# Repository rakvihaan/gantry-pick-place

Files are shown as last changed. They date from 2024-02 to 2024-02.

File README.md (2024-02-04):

# Gantry Robot for Diagnostics Laboratory Automation

A gantry robot built for automated archiving of vacuum tubes.


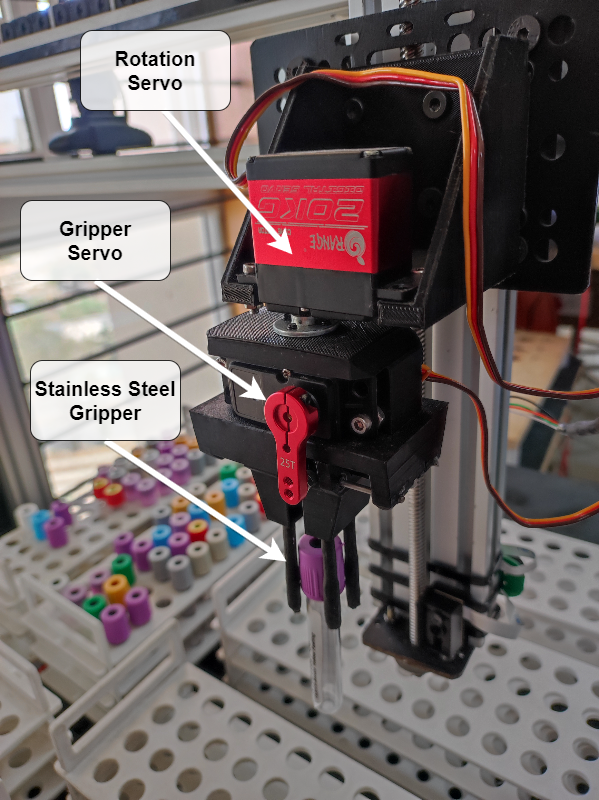
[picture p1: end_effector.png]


<br>
The hardware is built using aluminum extrusions and mild steel plates for various mounts.
Arduino Mega is used as the microcontroller with DRV8825 stepper motors drivers to drive the stepper motors.

This project also implements the application of object detection in identifying the vacuum tubes. The methodology involves training a model on annotated datasets, employing YOLO algorithm and PyTorch. Leveraging computer vision techniques, the system aims to accurately locate the vacuum tubes and the empty slots through real-time image feed.

- Has a workspace of 600 x 500 x 130 mm
- Three linear axes with a linear velocity range of
  - X-axis: 90-200 mm/s
  - Y-axis: 100-210 mm/s
  - Z-axis: 30-50 mm/s
- The three linear actuators and the wrist with the end effector with two degrees of freedom contribute to the 5-DOF design of the gantry robot
- The Z and Y axes are actuated using stepper motors and belt drive, while the X axis is actuated using a stepper motor and lead screw mechanism.
- A 3D printed end effector with stainless steel ends

## Python Scripts
- Clone the repo.
- Change pins and stepper motors speed and acceleration as per requirements in the [gantry.cpp](arduino_code/gantry.cpp) file.
- Upload the Arduino Code in the [arduino_code](arduino_code) folder.
- run the main.py file.
- Home the gantry before running any command.

## Future Improvements
- [ ] Replacing idler pulleys with optical encoders, can be used to keep track of the position.
- [ ] Replacing stepper motors with better motors with hugh torque at higher rpm.
- [ ] Realtime dynamic coordinates from image processing.
- [ ] Improve X-Axis to increase vertical workspace.

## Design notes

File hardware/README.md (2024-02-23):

# Hardware and Electrical Components BOM

| Item                               | Qty | Link |
| ---------------------------------- | :-: | :--: |
| **Hardware Components**            |     |      |
| Aluminum Extrusion                 |     |      |
| Delrin Roller Wheels               | 20  |      |
| T-nuts                             | 50  |      |
| Extrusion Brackets                 | 15  |      |
| GT2 Pulley                         |  3  |      |
| GT2 Idler Pulley                   |  3  |      |
| GT2 6mm width belt (2m)            |  2  |      |
| Lead Screw (8mm Pitch) (500mm)     |  1  |      |
| Lead Screw Block                   |  1  |      |
| Shaft Coupler                      |  1  |      |
| NEMA17 Motor mounts                |  4  |      |
| Idler Pulley mounts                |  3  |      |
| Z-Axis platform                    |  2  |      |
| 40mm Aluminium Spacers             |  3  |      |
| 90 deg Gantry bracket for Z-Axis   |  2  |      |
| Gantry bracket for Z-Axis          |  2  |      |
| 90 deg Extrusion Bracket           |  2  |      |
| Y-Axis Platform                    |  1  |      |
| X-Axis Platform                    |  1  |      |
| Servo bracket                      |  1  |      |
| Stainless Steel rods 3mm (75mm)    |  2  |      |
| Stainless Steel rods 1.2mm (100mm) |  2  |      |
| **Electrical Components**          |     |      |
| Stepper Motors (7.2 N-cm)           |  4  |      |
| DRV8825 Drivers                    |  4  |      |
| Limit Switches                     |  3  |      |
| CNC Shield                         |  1  |      |
| Arduino Mega                       |  1  |      |
| Barcode Scanner                    |  2  |      |
| Camera                             |  1  |      |
| Servos                             |  2  |      |

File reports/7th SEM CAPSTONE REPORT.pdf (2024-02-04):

(Established under Karnataka Act No. 16 of 2013) 100-ft Ring Road, Bengaluru – 560 085, Karnataka, India

### Report on Project

## “Archiving of Lab Samples using a Pick and Place Gantry robot in a Diagnostic Lab”

### Submitted by

Sumukh Marathe (PES1UG20EE068)
Vineet N Patil | (PES1UG20EE074)
N Ananya | (PES1UG20EE100)
Shreshta Srinivas (PES1UG20EE111)

### AUG - DEC 2023

Under the Guidance of
Dr. Venkatarangan MJ
Professor
Department of Electrical and Electronics PES University
Bengaluru

FACULTY OF ENGINEERING
DEPARTMENT OF ELECTRICAL AND ELECTRONICS
B. TECH IN EEE

FACULTY OF ENGINEERING

DEPARTMENT OF ELECTRICAL AND ELECTRONICS BACHELOR OF TECHNOLOGY

## CERTIFICATE

This is to certify that the Dissertation entitled

## “Archiving of Lab Samples using Pick and Place Gantry robot in a Diagnostic Lab”

Is a Bonafide work carried out by

Sumukh Marathe (PES1UG20EE068)
Vineet N Patil | (PES1UG20EE074)
N Ananya | (PES1UG20EE100)
Shreshta Srinivas (PES1UG20EE111)

In partial fulfilment for the completion of 7

th semester course work in the Program of Study
B. Tech in Electrical and Electronics Engineering (Embedded Systems) under rules and regulations of PES University, Bengaluru during the period Aug 2023 – Dec 2023. It is certified that all corrections/suggestions indicated for internal assessment have been incorporated in the report. The dissertation has been approved as it satisfies the 7th semester academic requirements in respect of project work.

### DECLARATION

We Sumukh Marathe (PES1UG20EE068), Vineet N Patil (PES1UG20EE074),N Ananya (PES1UG20EE100) and Shreshta Srinivas P R (PES1UG20EE111) hereby declare that the project entitled, “Archiving of Lab Samples using Pickand Place Gantry robot in a Diagnostic Lab”, is an original work done by us underthe guidance of Dr.Venkatarangan M J, Professor, Dept. of EEE, and is being submitted in fulfilment of the requirements for completion of 7th Semester course work in the Program of Study B.Tech in Electrical and Electronics Engineering.

PLACE: BENGALURU
DATE:

### ACKNOWLEDGMENT

We extend our deep sense of gratitude and sincere thanks to our chairman Dr.
M. R. Doreswamy (Founder, Chancellor – PES University), Prof. Jawahar Doreswamy, Pro-Chancellor of PES University and Dr. J Surya Prasad, the Vice Chancellor of PES University for giving us an opportunity to be a student of this reputed institution.

We extend our respect to our Principal Dr. K.S. Sridhar for his valuablesupport to conduct this Project under PES institution.

It is our privilege to thank the Chairperson of the Department Dr. Keshavan B.K., department of Electrical and Electronics Engineering for his support and guidance for doing our Project.

We express our sincere gratitude to our guide Dr. Venkatarangan M J for his valuable guidance and suggestion, technically and logically for doing our Project work.

We also express our gratitude to all our faculty members, parents and fellow mates who have helped us to carry out this work. Last but not the least, We thank almighty God for his blessings showered on us during this Project period.

### ABSTRACT

Archiving lab samples within a diagnostic laboratory involves the identification, labelling, and preservation of diverse bodily fluids or tissues for future reference. Adhering to precise protocols is essential in ensuring the integrity of archived samples, as human involvement may introduce inaccuracies. To address this concern, an automated robot has been developed through collaboration with and funding from Anand-Neuberg Diagnostics.

Gantry robots, also known as linear robots, are a type of industrial robot specifically designed for tasks such as picking and placing, assembly, and inspection across various industries. The objective of this project is to create and implement a gantry robot for a pick-and-place application, specifically for archiving vacuum tubes within a diagnostic laboratory. The robot operateswithin a flexible workspace, executing tasks such as picking, scanning, and placing vacuum tubes into designated crates.

The project initially utilised a Gantry Robot for transferring vacuum tubes between trays. An end effector, equipped with a precise gripper, was developed to ensure accurate pick-and-place movements. The robot's control system was optimised to delicately handle vacuum tubes, considering the spacing between tubes in the tray to prevent disruptions to adjacent samples.

Gantry robot is fabricated with the needed hardware and software interfaces. In terms of hardware, the robot needed a camera and bar-code scanner as sensors while the actuation is based on stepper motors with 5 degrees of freedom. Limit switches have been added for ensuring that it goes to a homing position on every restart of the system.

This project also implements the application of object detection in identifying the vacuum tubes. The methodology involves training a model on annotated datasets, employing YOLO algorithm and PyTorch. Leveraging computer vision techniques, the system aims to accurately locate the vacuum tubes and the empty slots through real-time image feed.

A 5 DOF gantry robot was designed and built using aluminium extrusion which helps in archiving of the vacuum tubes from 4 source racks to 5 destination racks, using Digital Image Processing. The tubes are picked, scanned and placedin their designated slots by the order of the Library Information System (LIS). The average cycle time to achieve the mentioned application is 20 seconds.

### CONTENTS

1. INTRODUCTION | 8
1.1. BACKGROUND | 8
1.2. PROBLEM STATEMENT | 8
1.3. OBJECTIVES/DELIVERABLES | 8
1.4. ARCHIVING & ITS SIGNIFICANCE | 8
2. LITERATURE SURVEY | 9

### 3. USE CASES FOR THE PROJECT AND COMPONENT

IDENTIFICATION | 12
3.1. ARCHIVING FUNCTIONALITY OF THE PROPOSED PROJECT | 12
3.2. USE CASE STEPS FOR PICK AND PLACE | 13
4. HARDWARE AND SOFTWARE ARCHITECTURE | 14
4.1. BLOCK DIAGRAMS | 14
4.2. MECHANICAL STRUCTURE AND OBJECTS | 15
4.2.1. HARDWARE USED | 16
4.2.2. SOFTWARE USED | 17
4.3. EVOLUTION OF END EFFECTOR | 17
5. ROBOT FABRICATION EXPENSES | 20
6. SW TOOLS AND HW INFRASTRUCTURE | 22
6.1. SW TOOLS | 22
6.2. MICROCONTROLLER, ACTUATORS AND SENSORS | 23
6.3. DESIGN PARAMETERS FOR AXES | 30
7. DATASET GENERATION | 31
8. OBJECT DETECTION | 33
8.1. ONE STAGE OBJECT DETECTORS | 33
8.2. WORKING OF YOLO | 35
8.2.1. RESIDUAL BLOCKS | 35
8.2.2. BOUNDING BOX REGRESSION or NON-MAXIMAL SUPPRESSION (NMS) | 35
8.2.3. INTERSECTION OF UNION | 36
8.3. YOLO MODELS | 36
8.4. YOLOV5 MODEL VERSIONS | 37
8.5. REAL TIME DETECTION OF VACUUM TUBES | 38
8.6. GENERATION OF MATRIX USING PYTHON CODE | 39
9. SOFTWARE FLOWCHART | 40
10. RESULTS | 41
10.1. GANTRY | 41
10.2. RECORDINGS | 43
10.3. CONSTRAINTS OBSERVED | 43
11. CONCLUSION | 44
12. FUTURE SCOPE | 44
13. REFERENCES | 44

TABLE OF FIGURES

Figure 1 - Moving table in X axis and couple of linear bearing on sides | 11
Figure 2 - General Block Diagram | 15
Figure 3 - Detailed Block Diagram | 15
Figure 4 - 3D view | 16
Figure 5 - Rack | 16
Figure 6 - Vacuum Tube | 16
Figure 7 – Initial End Gripper | 18
Figure 8 – Final End Gripper | 19
Figure 9 – End Gripper | 19
Table 1 - Cost Chart | 21
Figure 10 – Stepper Motor | 25
Figure 11 – Servo Motor | 25
Figure 12 – Arduino Mega | 26
Figure 13 – CNC Shield | 26
Figure 14 – DRV 8825 Driver | 27
Figure 15 – Inside a Limit Switch | 28
Figure 16 – Mechanical Limit Switch | 28
Figure 17 – AmazonBasics Camera | 29
Figure 18 – Barcode Scanner | 29
Figure 19 - Annotation by drawing bounding boxes | 32
Figure 20 - Preprocessing | 32
Figure 21 - Augmentation | 33
Figure 22 - One stage object detectors | 34
Figure 23 - Two stage object detector | 34
Figure 24 – Residual Blocks | 35
Figure 25 – Bounding Box | 36
Figure 26 - Performance Comparison | 37
Figure 27 - YOLO Model Comparison | 37
Figure 28 - Results obtained after training the YOLO v5x model for 195 epochs | 38
Figure 29 - Real time detection of tubes | 38
Figure 30 – Matrix Generated | 39
Figure 31 - Software Block diagram | 40
Figure 32 - Side view | 41
Figure 33 - End Gripper | 41
Figure 33 - Z axis | 42
Table 2 - Cycle time recordings | 43
Table 3 - Trials | 43

Archiving of Lab Samples using Pick and Place Gantry robot in a Diagnostic Lab

Dept. of Electrical & Electronics Engineering, PES University | Page 8

### 1. INTRODUCTION

### 1.1. BACKGROUND

In a diagnostic laboratory, vacuum tube samples are routinely collected from patients to perform various medical tests to diagnose diseases, monitor disease progression,and assess treatment effectiveness. These samples could include blood, urine, cerebrospinal fluid, sputum, and other bodily fluids or tissues.

The archiving of vacuum tube samples refers to the process of preserving these samples for future reference or analysis. This is important because, in some cases, it may be necessary to retest a sample or compare it with previous test results to detect changes in the patient's condition or disease progression.

### 1.2. PROBLEM STATEMENT

It is important to follow proper protocols for archiving samples to ensure their integrity. This includes labelling each sample with a unique identifier, storing them in a secure and temperature-controlled environment, and tracking their location and storage duration. Human involvement might result in inaccuracies. This system shouldaddress the challenges such as precise tube identification, safe handling, quicker operation, and seamless integration with existing laboratory workflow. To resolve this we are developing an automated gantry robot.

### 1.3. OBJECTIVES/DELIVERABLES

- Utilising Image Processing with Machine Learning techniques, a highly effective gantry robot for vacuum tubes
- Faster and extremely accurate archiving of samples
- Reduction of human workload

Dept. of Electrical & Electronics Engineering, PES University | Page 9

### 1.4. ARCHIVING & ITS SIGNIFICANCE

The significance of archiving lab samples lies in the fact that they can be used for further research or analysis in the future. For example, if new testing methods or technologies are developed, samples can be retrieved from the archive and analysed using the new methods, potentially leading to new insights or discoveries. Additionally, samples may be needed for quality control purposes, such as to verify the accuracy and consistency of test results over time.

Archiving lab samples is also important for meeting regulatory requirements and ensuring the integrity of research data. In many cases, regulatory agencies require that samples be retained for a certain period of time as part of the documentation process. Archiving samples can also help prevent data loss due to equipment failure, natural disasters, or other unforeseen events.

There are several reasons why archiving is important in a diagnostic lab:

a. Quality control: Archiving helps to ensure the accuracy and reliability of test results by providing a record of previous test results and enabling the lab to monitor and track the performance of its testing procedures and equipment over time.
b. Compliance: Many regulatory agencies require diagnostic labs to maintain accurate records of their testing processes and results, and failure to do so can result in fines, legal liability, or loss of accreditation.
c. Research and development: Archiving can provide a valuable resource for researchers and developers working on new diagnostic tests and treatments. By maintaining a comprehensive archive of patient samples and data, labs can contribute to the development of new treatments and therapies that could benefit patients in the future.
d. Patient care: Archiving allows for the ongoing monitoring of patient healthand provides a valuable resource for healthcare providers to make informed decisions about patient care based on previous test results and medical history.

Dept. of Electrical & Electronics Engineering, PES University | Page 10

### 2. LITERATURE SURVEY

Paper [1] : "Evolution of YOLO-V5 Algorithm for Object Detection: Automated Detection of Library Books and Performance validation of Dataset,"

The paper discusses the implementation and evaluation of the You Only Look Once (YOLO) version 5 algorithm for object detection, specifically for the automated detection of library books. The authors explain the steps involved in the training of the YOLOv5 algorithm using a dataset of library book images. The dataset was created by capturing images of library books using a smartphone camera and manually labelling them. The trained model was then evaluated for its performance on the detection of library books. The authors report an average precision of 0.9535 for the YOLOv5 algorithm. They conclude that the YOLOv5 algorithm is an efficient and accurate tool for automated object detection and can be used in various applications, including library book detection.

Paper[2] : “Object Detection Method for Grasping Robot Based on Improved YOLOv5”

The paper proposes a new object detection method for a grasping robot based on the improved YOLOv5 (You Only Look Once version 5) algorithm. The authors argue that the traditional YOLOv5 algorithm has limitations in detecting small objects and lacks robustness in complex scenarios. To address these limitations, the authors propose an improved YOLOv5 algorithm that incorporates a new loss function and a focal loss function to improve the accuracy of small object detection. They also introduce a multiscale feature fusion module to enhance the robustness of the model in complex scenarios. The proposed method is evaluated on a dataset of real-world objects, and the results show that the improved YOLOv5 algorithm outperforms the traditional YOLOv5 algorithm and other state-of-the-art object detection methods in terms of accuracy and efficiency. The authors demonstrate the feasibility of the proposed method by integrating it into a grasping robot system and conducting experiments on object grasping tasks.

Dept. of Electrical & Electronics Engineering, PES University | Page 11

Paper[3] : "Laboratory gantry robot design and control"

The paper focuses on the design and control of a laboratory gantry robot, which is a type of robotic system that is used for various applications such as material handling, assembly, and testing in a laboratory environment. The authors describe the overall design of the gantry robot and its mechanical structure, including the motors, bearings, and other mechanical components. The paper then discusses the control system of the gantry robot, which involves the use of a programmable logic controller (PLC) and a personal computer (PC). The authors describe the software architecture used to control the gantry robot, which includes a user interface for setting up the system and defining the robot's movements. The authors also present experimental results that demonstrate the gantry robot's capabilities, including its speed, accuracy, and repeatability. The results show that the gantry robot is capable of performing various tasks with high precision and reliability. Overall, the paper provides a detailed description of the design and control of a laboratory gantry robot and highlights its potential use in various laboratory applications. The paper may be of interest to researchers and engineers working in the field of robotics and automation.

Figure 1 - Moving table in X axis and couple of linear bearing on sides

Dept. of Electrical & Electronics Engineering, PES University | Page 12

Paper[4] : "RealTime Object Detection using Machine Learning"

The paper describes a real-time object detection system based on machine learning. The proposed system uses a Convolutional Neural Network (CNN) architecture to detect and classify objects in real-time. The system is designed to work with live video streams and can detect objects in real-time without any lag. The authors of the paper conducted several experiments to evaluate the performance of the proposed system. The results of the experiments showed that the proposed system is capable of detecting objects accurately and quickly, making it suitable for real-time applications such as video surveillance and autonomous vehicles. In conclusion, the paper presents a realtime object detection system based on machine learning that can detect and classify objects in real-time with high accuracy. The proposed system has the potentialto be used in a variety of applications, including video surveillance, autonomous vehicles, and robotics.

Paper[5] : "Pick and place industrial robot controller with computer vision"

The paper proposed a system for controlling an industrial robot using computer vision to perform pick-and-place operations. The system consists of a camera that captures images of the work environment and a controller that processes the images to detect objects and determine their positions. The controller then generates commands for the robot to perform the necessary actions. The authors demonstrated the effectiveness of their system through experiments, which showed that it could accurately detect and manipulate objects in real time.

Paper[6] : "Material Handling Using Pick and Place Robot"

The paper proposed a system for material handling using a pick-and-place robot. The system consists of a robot arm that can be controlled using a computer interface, which allows the user to specify the desired pick-and-place operations. The system also includes a conveyor belt that feeds materials to the robot, and sensors that detect the presence and position of the materials. The authors demonstrated the effectiveness of their system through experiments, which showed that it could accurately and efficiently handle materials of different shapes and sizes. The proposed system has potential applications in manufacturing and warehouse automation.

Dept. of Electrical & Electronics Engineering, PES University | Page 13

### 3. USE CASES FOR THE PROJECT AND COMPONENT IDENTIFICATION

### 3.1. ARCHIVING FUNCTIONALITY OF THE PROPOSED

PROJECT

The proposed project manages use of thoughts learnt in different papers that includes building a robot which includes utilisation of Computer Vision for detecting the vacuum tubes and to decide which destination rack to place it in. In general, elements of the robot have been made strong and fast, the robot is made of aluminium, fulfillingthe necessity of strength and speed ready to play out the archiving process with ideal proficiency.

The vacuum tube archiving robot model comprises of the following :

- 3 Linear actuators (1 lead screw, 2 belt drives)
- 4 NEMA-17 stepper motors
- 2 Servo motors
- Arduino Mega
- CNC Shield
- 4 DRV8825 stepper motor driver
- 3 Mechanical limit switches
- End effector with a precise gripper
- Power supply (24V)
- Camera (Amazon Basics)
- Barcode Scanner
- Aluminium Framework

Dept. of Electrical & Electronics Engineering, PES University | Page 14

### 3.2. USE CASE STEPS FOR PICK AND PLACE

As referenced already, the entire task depends on:

Software: Image processing and Machine Learning
Hardware: Motors and Actuators

Stage 0: This stage involves homing of each axis (x,y,z) to the base coordinate (0,0,0) which is identified with the help of mechanical limit switches attached to the framework. The actuators move in one specified direction until it hits the limit switch which is then described as the base coordinate. From here, the coordinate system for the whole workspace is defined, taking the base coordinate as the reference.

Stage 1: The camera captures a real time image of two source racks at a time. This image is analysed to produce a matrix with information on the vacuum tubes' presence. Beginning with the vacuum tube location, the actuators use this matrix as aninput to start the cycle, which saves time by not having to walk through every slot in the rack. This data is transformed into the coordinate frame using forward kinematics and the actuators move accordingly to pick up the vacuum tube for the next step of thecycle.

Stage 2: Once the vacuum tube is picked, the barcode scanner attached to the framework scans the barcode present on the side of the vacuum tube. The scanned data is integrated with the LIS (Library Information System) provided by the laboratory. This serves as a verification system to record every sample.

Stage 3: Subsequent to picking the vacuum tube, the LIS provides information about the destination rack where the vacuum tube is supposed to be placed and also the slot of that rack. This software records and archives the location, status and medical data of the sample. A new case emerges when the vacuum tube has not gone through all the tests for which there is a designated rack to the vacuum tube.

Stage 4: The vacuum tube is then taken to the rack and slot given by the LIS with the help of the actuators and is placed. The entire cycle is restarted with the next vacuum tube of the source rack.

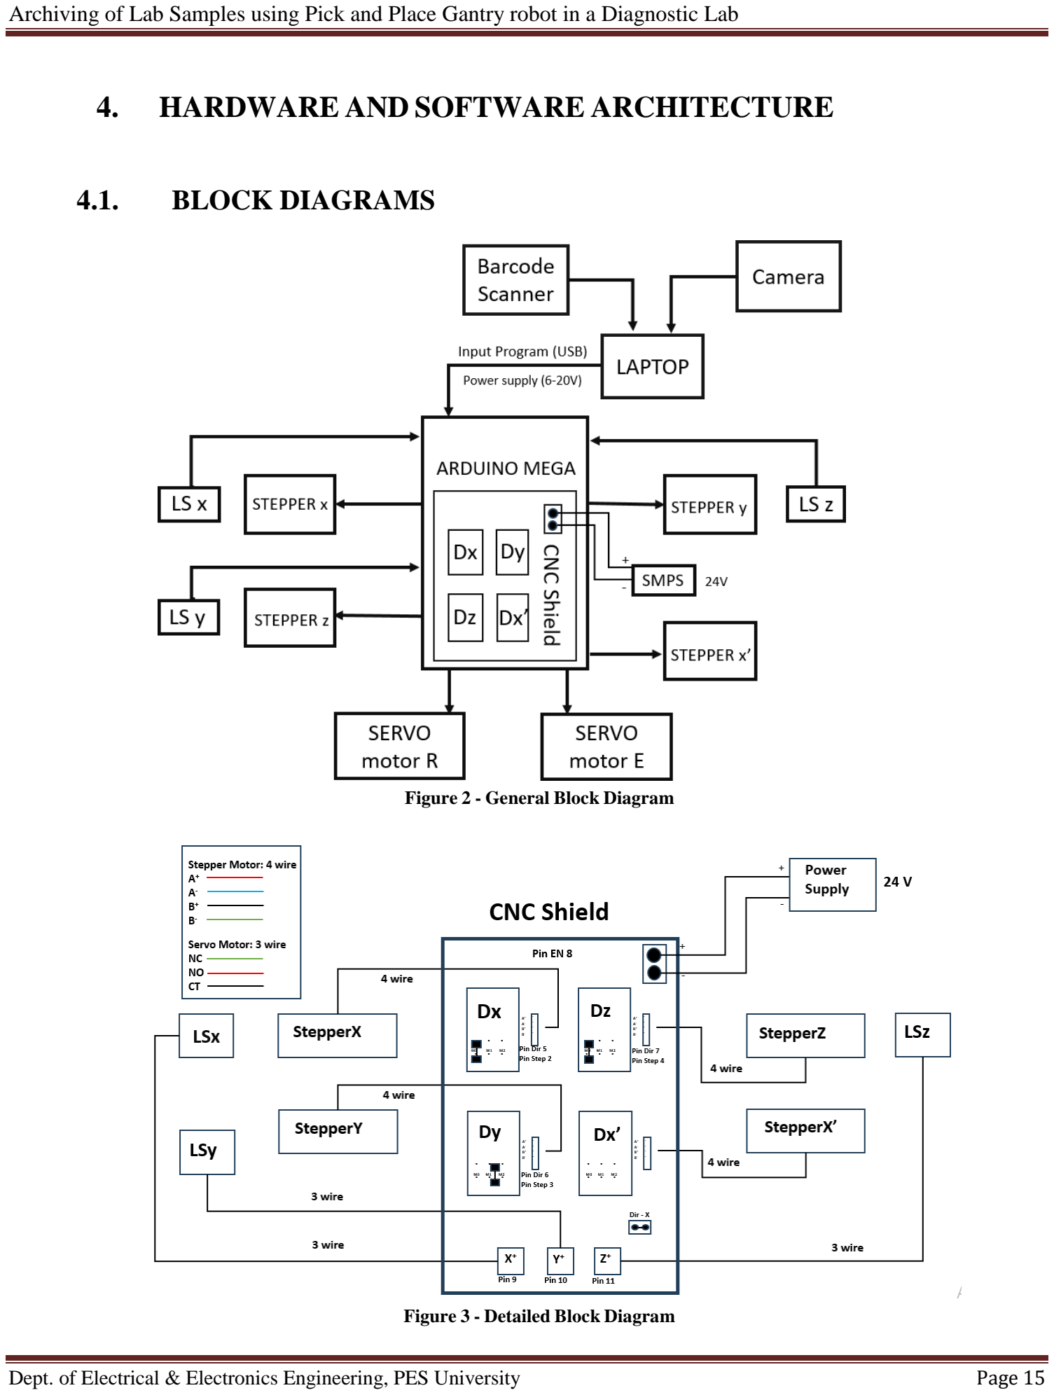
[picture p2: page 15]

Dept. of Electrical & Electronics Engineering, PES University | Page 15

### 4. HARDWARE AND SOFTWARE ARCHITECTURE

### 4.1. BLOCK DIAGRAMS

Figure 2 - General Block Diagram

Figure 3 - Detailed Block Diagram

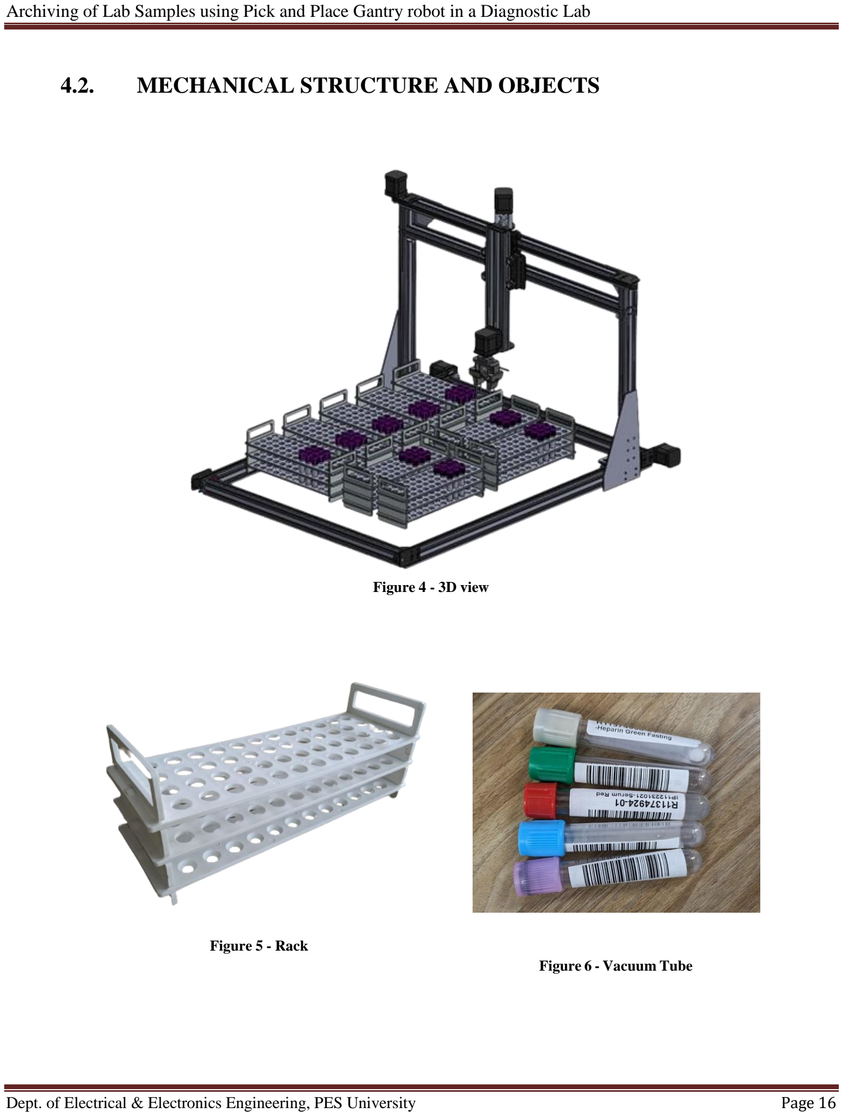
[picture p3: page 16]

Dept. of Electrical & Electronics Engineering, PES University | Page 16

### 4.2. MECHANICAL STRUCTURE AND OBJECTS

Figure 4 - 3D view

Figure 5 - Rack
Figure 6 - Vacuum Tube

Dept. of Electrical & Electronics Engineering, PES University | Page 17

### 4.2.1. HARDWARE USED

1. Stepper and Servo Motors
2. Arduino Mega
3. CNC Shield
4. Motor Drivers
5. Limit Switches
6. Barcode Scanner
7. AmazonBasics Camera
8. Linear Actuators - Belt Drive & Lead Screw
9. Aluminum Extrusions

### 4.2.2. SOFTWARE USED

1. Python
2. Python OpenCV
3. Arduino IDE

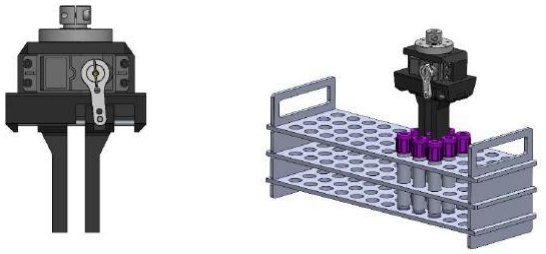
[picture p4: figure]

Dept. of Electrical & Electronics Engineering, PES University | Page 18

### 4.3. EVOLUTION OF END EFFECTOR

To design and fabricate an end effector to be able to pick and place the test tubes during the archiving process while being able to withstand the speed of the Gantry System and avoid disturbing the neighbouring test tubes in the tray.

The end effector stands as a pivotal element within robotic systems, functioning as the tactile interface between the machine and its operational environment. It can also be defined as the final end of any robotic system that interacts with real world objects and needs to be able to conceive and work seamlessly, encompassing functions suchas gripping, manipulating, cutting, or painting.

The end effector's adaptability is key, permitting seamless tool interchangeability for a diverse array of tasks without necessitating extensive structural modifications. Furthermore, its influence resonates in the realm of accuracy, as advanced sensors and control mechanisms enhance the robot's ability to perform tasks with utmost precision.

The end effector was designed in SolidWorks, a few different mechanisms were proposed and improved upon and the finalised end effector was 3D printed using PLA plastic. For the actuator itself, a servo motor was chosen as they have higher angular accuracy. The end effector features four prongs made of stainless steel on the end which grabs onto the test tubes with ease.

Figure 7 – Initial End Gripper

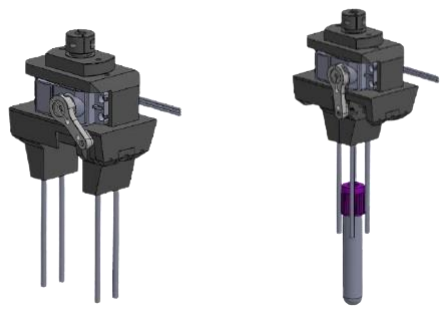
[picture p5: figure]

Dept. of Electrical & Electronics Engineering, PES University | Page 19

Figure 8 – Final End Gripper

Figure 9 – End Gripper

Dept. of Electrical & Electronics Engineering, PES University | Page 20

### 5. ROBOT FABRICATION EXPENSES

SL NO. | COMPONENTS | QUANTITY | TOTAL COST
1 | Aluminium Extrusion | 6.5m | 2810
2 | Angle brackets | 30 | 850
3 | Laser cutting | 18 | 3300
4 | NEMA 17 Stepper motors | 4 | 5089
5 | Servo motors | 2 | 1440
6 | Arduino Mega | 1 | 1450
7 | CNC Shield | 1 | 150
8 | Motor Drivers DRV8825 | 4 | 600
9 | Limit Switches | 3 | 150
10 | Power Supply (SMPS) | 1 | 900
11 | Lead Screw | 300mm | 250
12 | Belt | 5m | 330
13 | Aluminium Spacer | 3 | 54
14 | Solid V Wheel Kit | 20 | 2300
15 | GT2 Idler Pulley | 4 | 500
16 | GT2 Pulley 30 teeth | 4 | 620
17 | Eccentric Spacer | 12 | 350
18 | Anti Vibration Feet | 4 | 150
19 | Spiral Wrapping Band | 4m | 42
20 | Cable Carrier | 4m | 1000
21 | AmazonBasics Camera | 1 | 1100
22 | Barcode Scanner | 1 | 2890
23 | 3D Printed Slots | 20 | 3100

Dept. of Electrical & Electronics Engineering, PES University | Page 21
24 | End Effector | 1 | 1040
25 | Nuts | 120 | 1200
26 | Screws & Spanner | NA | 2004
27 | Plywood | 600 x 400 mm | 550
28 | Wires | 8m | 500
29 | Miscellaneous | NA | 1000

TOTAL COST - 35,719

Table 1 - Cost Chart

Dept. of Electrical & Electronics Engineering, PES University | Page 22

### 6. SW TOOLS AND HW INFRASTRUCTURE

### 6.1. SW TOOLS

### 1. Python

Python is a vigorous and versatile programming language that is likewise exceptionally basic for novices to learn. There aren't numerous intricate ideas to stressover, and its punctuation is clear. Python is also used extensively in machine learning and artificial intelligence, which are becoming increasingly important in robotics.

### 2. Arduino IDE

The Arduino IDE (Integrated Development Environment) is a platform used to develop software for Arduino boards. It is an open source platform which provides an interface to integrate hardware and software to create efficient and innovative projects.Using Arduino IDE, we can write, edit, compile and even upload code to any Arduino microcontroller board which can be used with every model. The Arduino IDE is a C based language with an integrated version of C++ which uses simple syntax making it user friendly and thus provides a very simplified platform to handle projects and programs.

### 3. YOLO

YOLO (You Only Look Once) is a real time object detection algorithm that detects and identifies different objects in an image. The YOLOv5x gives us the class probability for the detected objects as it performs as a regression problem. The real time object detection in the YOLOv5x algorithm is based on Convolutional Neural Networks (CNN). Accordingly, the algorithm needs only one propagation through the neural network to detect objects. Thus the prediction of the whole image is finished by just one algorithm. Using this, the CNN is used to simultaneously determine the probabilities and bounding boxes for different classes.

Dept. of Electrical & Electronics Engineering, PES University | Page 23

### 6.2. MICROCONTROLLER, ACTUATORS AND SENSORS

### 1. Actuators

An actuator is a mechanical or electrical device that is responsible for converting energy into motion. Its purpose is to control or move a system or mechanism, such as a valve or a motor, in response to an input signal. The driven actuators system has various options in the field of linear motion due to the advancements in the Engineering field. Among them, the most used type of drive systems include the conversion of rotary motion to linear motion which uses lead screw and belt drive. The mentioned options play a significant role in the actuator system

### 1.1 Belt Drive Actuator

The rotation motion is transferred from one shaft to another with the help of a belt drive actuator provided the two shafts are running at the same or variable speed. The construction includes a belt at high tension connected between two or more pulleys. We have made use of a V belt which has a trapezoidal cross section which is used in a grooved pulley. This forms the X and Y axis of our gantry robot.

The following details are required for modelling a kinematics model of a belt linear actuator :
- Linear belt actuator length (L)
- Stepper motor steps per revolution (N)
- Pulley diameter (D)
- Micro-step resolution (μ): (e.g., 1/8, 1/16, 1/32, etc.)

The simple equations to find the displacement per micro-step and steps required to move the actuation per unit displacement respectively are:

d_microstep = (L / (N * π * D)) / μ N_microsteps = D_desired / d_microstep

Dept. of Electrical & Electronics Engineering, PES University | Page 24

### 1.2 Lead Screw Actuator

The rotation motion is converted into linear motion with the help of a mechanical linear actuator, i.e., lead screw actuator. It has no ball bearing between the nut threads while the working involves the sliding of the screw shaft. These are mostly used in vertical applications as they are found to be efficient in such scenarios. An important property of some lead screw actuators include no braking system as they are capable of self locking. We used this actuator for our Z axis on the gantry robot.

The following details are required for modelling a kinematics model of a lead screw linear actuator :
- Linear lead screw pitch (P) (distance travelled in one complete revolution)
- Linear actuator length (L)
- Stepper motor steps per revolution (N)

The simple equations to find the displacement per micro-step and steps required to move the actuation per unit displacement respectively are :

d_step = P / N
N_steps = D_desired / d_step

### 2. Stepper Motors

A stepper motor is a type of electric motor that is designed to rotate in precise increments or steps, rather than continuously. Each step corresponds to a fixed angular rotation, and the motor can be controlled to move forward or backward one step at a time.

The NEMA 17 stepper motor is a type of hybrid stepper motor which means it combines features of both permanent magnet and variable reluctance motors. It has two main components: a rotor, which is the rotating part of the motor, and a stator, which is the stationary part of the motor. The rotor of the NEMA 17 stepper motor typically has 50-200 teeth or poles, depending on the specific model. The stator has multiple coils of wire that are energised in sequence to create a rotating magnetic field,which causes the rotor to rotate in precise steps.

For our application of actuation, we are using 4 NEMA 17 motors. Two for the movement of the X axis, one for the movement of the Y axis, one for the movement of the Z axis.

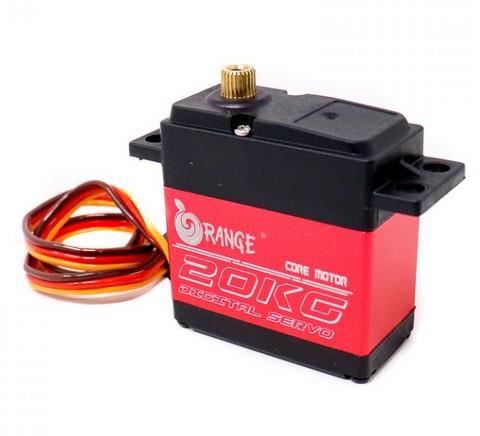
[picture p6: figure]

Dept. of Electrical & Electronics Engineering, PES University | Page 25

Figure 10 – Stepper Motor

### 3. Servo Motors

Servo motors are rotary actuators which are capable of accurate angular or linear position and acceleration control in a mechanical system. It has an inbuilt sensor which provides feedback coupled to the motor. In our application, two servo motors are being used. One for the rotation of the end effector and another for the movement of the opening and the closing of the gripper.

The model we are using is OT5320M which has the following specifications:

- Torque = 16.5 kg cm
- Speed = 54 RPM
- Voltage rating = 6V
- Current rating = 2.3A

Figure 11 – Servo Motor

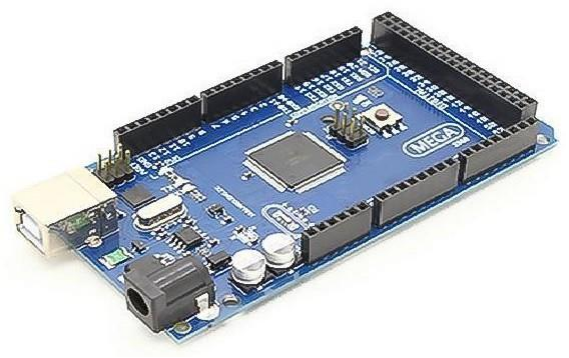
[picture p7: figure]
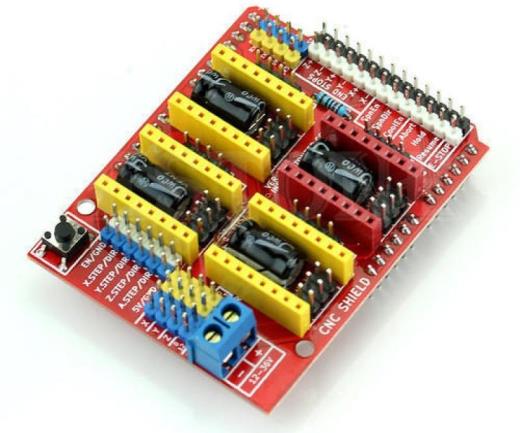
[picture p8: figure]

Dept. of Electrical & Electronics Engineering, PES University | Page 26

### 4. Arduino Mega

The Arduino Mega 2560 is based on a ATmega250 microcontroller. It consists of 16 analog inputs, 54 digital pins which can be used for input or output, 4 hardware serial ports (UARTs) and a 16 MHz crystal oscillator, power jack port with a reset button. We felt this was a suitable micro-controller due to its features that meet our requirements.

Figure 12 – Arduino Mega

### 5. CNC Shield

The CNC shield for Arduino has a compact design best suited for UNO or MEGA boards compatible with arduino. It features a 4-Axis support (X, Y, Z or A which can duplicate X, Y, Z or do a full 4th axis with custom firmware using pins D12 and D13). This CNC shield for arduino is most commonly used as a component in DIY 3D. This shield enables us to connect the arduino to the individual drivers and its functionalities help us control all the actuators. The Shield is placed on the Arduino microcontroller and the drivers are mounted on this shield. The motors are also connected through the connector pins provided by the CNC shield.

Figure 13 – CNC Shield

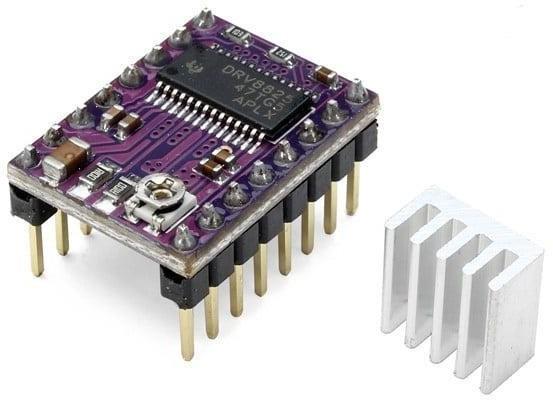
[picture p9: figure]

Dept. of Electrical & Electronics Engineering, PES University | Page 27

### 6. Motor Drivers

We use the stepper motor driver DRV8825. It can be mounted on the CNC Shield. It is a microstepping stepper motor driver that can control bipolar stepper motors. It supports up to 1/32 microstepping, allowing for smoother motion and finer control of the stepper motor. It allows you to set the motor current by adjusting a potentiometer on the driver board. This helps in optimising the motor performance and avoiding overheating.

It includes overcurrent and overtemperature protection to prevent damage to the motor and driver under certain conditions.The driver receives step and direction signals from a microcontroller or other control source to determine the motor movement. It is designed for use with bipolar stepper motors, which have two coils. These motors are commonly found in various applications like 3D printers, CNC machines, and robotics. It can operate in a voltage range suitable for the connected stepper motor.

The specifications are:

- Voltage setting = 0.6V
- Current setting = 1.2A
- Microstep Resolutions = full, 1/2, 1/4, 1/8, 1/16, and 1/32

Figure 14 – DRV 8825 Driver

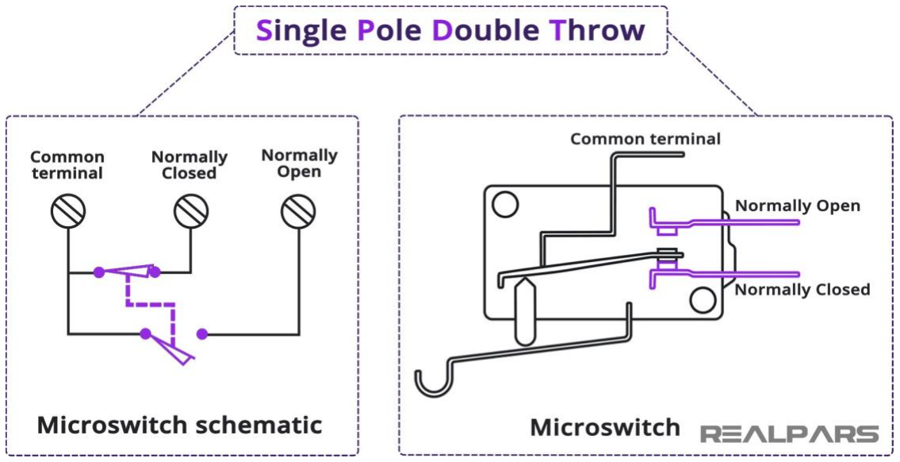
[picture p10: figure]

Dept. of Electrical & Electronics Engineering, PES University | Page 28

### 7. Limit Switches

Mechanical limit switch is a device that detects the physical position of an object. It typically consists of an actuator and contacts that open or close when the object reaches a specific point, triggering an electrical signal. A micro switch consists of dualswitches which operate together by sharing a common terminal. Among them, one of the switches is normally closed while the other is normally opened. This switch configuration is called Single Pole Double Throw (SPDT). The following working diagram shows a dotted line which represents that both the switches are mechanically connected. Hence, they operate at the same time.

Figure 15 – Inside a Limit Switch

Figure 16 – Mechanical Limit Switch

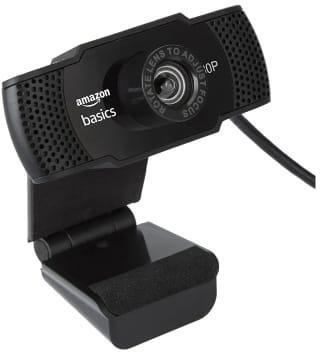
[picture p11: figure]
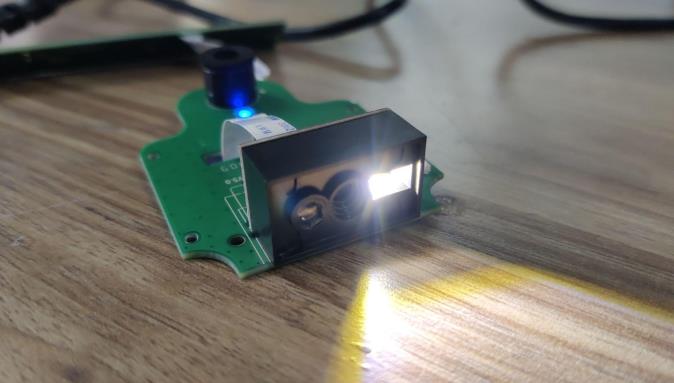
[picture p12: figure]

Dept. of Electrical & Electronics Engineering, PES University | Page 29

### 8. Camera

A digital camera is a device that captures photographs in digital memory. Using a USB protocol, this photo is transferred to our system where it can be processed. It is mounted on the framework where it can be moved which allows us to take a clear image of the source racks. We tried this operation with various models but we found the best suitable model as the AmazonBasics camera.

Figure 17 – AmazonBasics Camera

### 9. Barcode Scanner Module

A barcode scanner module is an ocular scanner which is capable of reading barcodes which are printed on objects. The scanned data is transferred to a computer. It consists of a light source, a lens and a light sensor which converts optical impulses to electrical signals. We are using this as it has a lot of programmable features which are suitable for our application. This is mounted on the framework as it is easier to scan the picked up vacuum tube.

Figure 18 – Barcode Scanner

Dept. of Electrical & Electronics Engineering, PES University | Page 30

### 6.3. DESIGN PARAMETERS FOR AXES

To model a kinematics model and control system to control the Gantry System, to ensure seamless operation and synchronisation.

The kinematics model of a system describes the relationship between the inputs, the resulting position and orientation of the system's end effector or tool. It enables the prediction and calculation of the system's position, velocity, and acceleration based on the actuator inputs. This model is crucial for controlling and programming the gantry system's motion to achieve desired trajectories, positions, and orientations. The kinematics model of a system enables tasks such as trajectory planning, path generation, collision avoidance, and real-time control. It plays a crucial role in robotics, automation, and CNC machining applications where precise positioning and motion control are essential.

The Gantry System, just like any mechanical automated systems, needs a mathematical model that tells the system how much each actuator has to be actuated toreach the desired position. This ensures precise operation given the size of the object to be picked and placed. This helps in motion planning and control of the gantry robot’s movement, as the payload, the vacuum tubes, are to be handled with care as they contain biological masses and need to be transported carefully throughout the archiving process without breaking the vacuum tube or spilling the contents of the vacuum tube. The model also affects the runtime of the operation in-turn affecting the whole workflow of the lab.

X axis

- Diameter of the pulley = 12.8mm
- Circumference of the pulley = πd = 40.212mm
- Number of pulses for one rotation for NEMA 17 = 200 pulses/rotation
- Microstep Mode = ½
- Distance moved per pulse = 40.212/400 = 0.1005 mm/pulse
- Steps per second = 2000
- Distance moved in one rotation = 60mm
- RPM of X axis = 300

Dept. of Electrical & Electronics Engineering, PES University | Page 31

Y axis

- Diameter of the pulley = 10.3mm
- Circumference of the pulley = πd = 32.358mm
- Number of pulses for one rotation in NEMA 17 = 200 pulses/rotation
- Microstep Mode = ¼
- Distance moved per pulse = 32.358/800 = 0.0404mm/pulse
- Distance moved in one rotation = 60 mm
- RPM of Y axis = 150

Z axis

- Diameter of the lead screw = 8mm
- Pitch of the lead screw = 2mm
- Steps per second = 8000
- Number of steps for one rotation = 400
- RPM of the Z axis = 1200

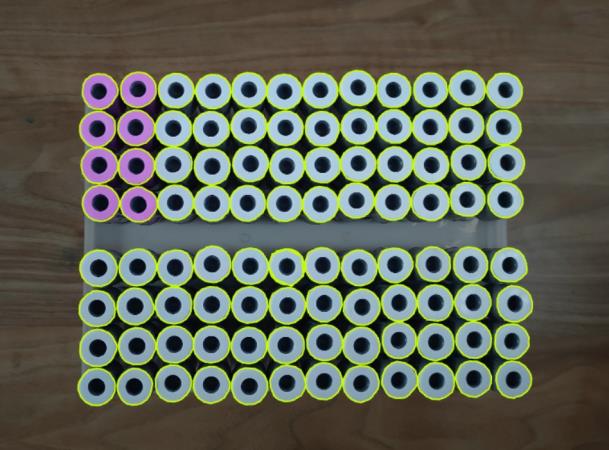
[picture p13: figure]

Dept. of Electrical & Electronics Engineering, PES University | Page 32

### 7. DATASET GENERATION

The dataset generation process involves capturing a real time object using a camera. In our application, the objects are EDTA Vacuum Tubes placed in the test tube racks. The first step involved annotating the images by drawing bounding boxes around the tube caps. The annotated images were converted to a Class depending on the presence of the vacuum tubes using the RoboFlow software. This software is specifically used for annotating as well as augmenting the image dataset.

Figure 19 - Annotation by drawing bounding boxes

The second step involves the images being split into train, test and validation dataset in the RoboFlow software. About 120 images were sent for the training model. The resizing of the images and auto orientation was performed in the preprocessing method. Thus, the output image is resized to 400 x 400 pixels because the maximum size YOLOv5x can take up is 640 x 640 pixels.

Figure 20 - Preprocessing

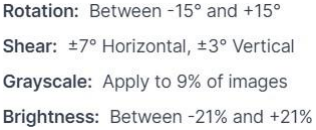
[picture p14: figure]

Dept. of Electrical & Electronics Engineering, PES University | Page 33

Data Augmentation is a method where it applies different types of parameters on the image to increase the dataset for better processing. Such parameters are:

Figure 21 - Augmentation

### 8. OBJECT DETECTION

The detection of the test tubes and localization of the captured image is done in YOLOv5x by using PyTorch. The YOLOv5x uses neural networks for the object identification process. It is specifically well known for its characteristics such as high accuracy, speed and training techniques. It makes the algorithm run faster as it is a one stage object detector. AS mentioned earlier, YOLO employs Convolution Neural Networks (CNN) which consists of 24 convolution layers and 2 fully connected layers that form the detection layer. It uses one neural network to process the whole image which later separates the processed image into small areas, further calculates the probabilities and the bounding boxes. The probability result depicts the weights of detected bounding boxes.

### 8.1. ONE STAGE OBJECT DETECTORS

The one stage object detectors deal with object detection as a regression problem. The output of this network includes the probability of classes and the coordinates of the bounding box from the captured image. This typical model omits the region proposal stage which is commonly referred as the region proposal network. This is found in the two stage object Detectors where these regions are marked as the region that contains the objects.

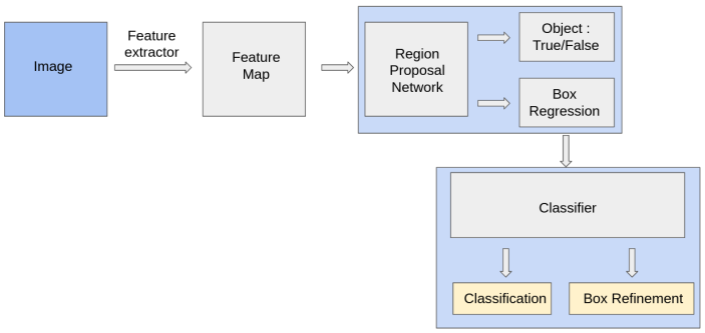
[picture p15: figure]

Dept. of Electrical & Electronics Engineering, PES University | Page 34

Figure 22 - One stage object detectors

Figure 23 - Two stage object detector

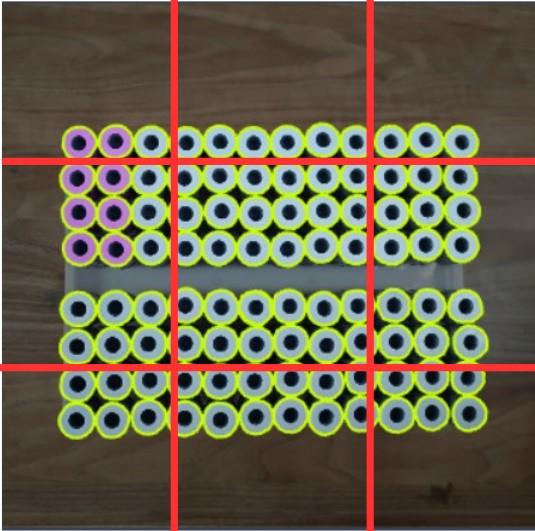
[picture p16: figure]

Dept. of Electrical & Electronics Engineering, PES University | Page 35

### 8.2. WORKING OF YOLO

YOLO makes use of 3 main steps for object detection.

1) Residual Blocks
2) Bounding box regression or Non-Maximal Suppression (NMS)
3) Intersection of union

### 8.2.1. RESIDUAL BLOCKS

The real time captured image is fed as the input. The image is split into multiple boxes of equal dimensions. The detected grid cells contain objects present inside each grid cell.

Figure 24 – Residual Blocks

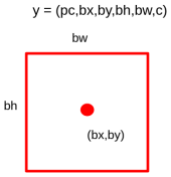
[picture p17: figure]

Dept. of Electrical & Electronics Engineering, PES University | Page 36

### 8.2.2. BOUNDING BOX REGRESSION or NON-MAXIMAL SUPPRESSION

(NMS)

Bounding boxes are drawn around the detected objects in the input image. The bounding boxes are characterised by different attributes such as height(bh), width(bw), class(c), probability of the object being in the box (pc) and x(bx), y(by) which forms the bounding box centre coordinates. YOLOv5x makes use of the regression technique on the bounded boxes to determine the values y=(pc,bx,by,bh,bw,c). It works on one condition, i.e if the probability value pc is less than the threshold, the bounding box is removed by the YOLO.

Figure 25 – Bounding Box

### 8.2.3. INTERSECTION OF UNION

Preceding the bounding box selection, YOLO uses IOU to draw an output bounding box which appears across the object. Each cell displays the bounding boxes and their confidence scores. The initial bounding boxes remain the same while the IOU turns one if predicted. The Intersection of Union discards the bounding boxes which are not of the same size as that of the actual box.

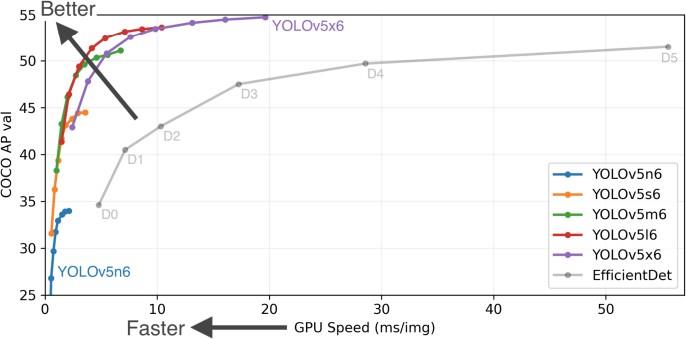
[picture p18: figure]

Dept. of Electrical & Electronics Engineering, PES University | Page 37

### 8.3. YOLO MODELS

Prominent improvements are seen through models ranging from v1 to v7. YOLO v1 is characterised for its object detection, confidence loss and division of grids. YOLO v2 model is employed with K-means, Two stage training model and a fully conventional network. YOLO v3 consists of multiscale detection integrated with Feature Pyramid Networks. MISH, a self-regulated non-monotonic activation function which performed better than Leaky ReLU, Spatial Pyramid Pooling, Generalised Intersectionover Union (GIOU) loss function as well as data enhancement Mosaic/Mixup was available in YOLO v4. We can enable flexible control of model size, application of Hardwish activation function, and data enhancement. The latest models of the YOLO family are the v6 and v7 which proved to be more precise and faster compared to the previous versions.

### 8.4. YOLOV5 MODEL VERSIONS

The YOLOv5 generates a range of pre-trained models. The comparison of the various YOLO models is a tradeoff between the times inferred to their model size. YOLO v5n is chosen to be the lightest version because of its small size of 4MB but has proven to be not very accurate. Compared to YOLOv5n, YOLOv5x is the most accurate of its family but with a large size of 168 MB.

Figure 26 - Performance Comparison

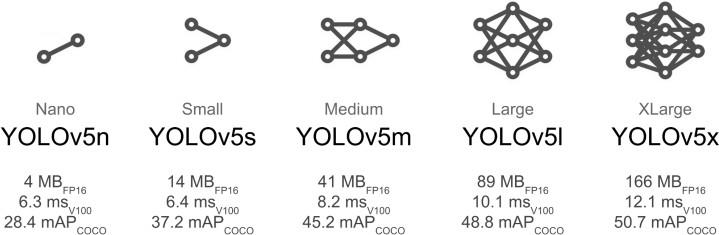
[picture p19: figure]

Dept. of Electrical & Electronics Engineering, PES University | Page 38

Figure 27 - YOLO Model Comparison (https://docs.google.com/document/d/1qMKxzotBbLhzuNvUcJ4rFbwgzjcFsYZf/edit#heading%3Dh.2grqrue)

### 8.5. REAL TIME DETECTION OF VACUUM TUBES

The YOLOv5x model is used to help the process of disassembly by the vacuum tube detection as YOLOv5x is proved to be the most accurate versions of its family. This is 36 implemented by feeding a dataset which consists of about 120 images in various positions and parameters like lighting conditions. The input image size of 400x400 and 18 training batch size were used in detecting the tubes for 195 epochs. Following results were obtained for 195 epochs after being trained by the YOLOv5x model.

Figure 28 - Results obtained after training the YOLO v5x model for 195 epochs

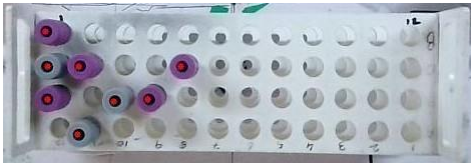
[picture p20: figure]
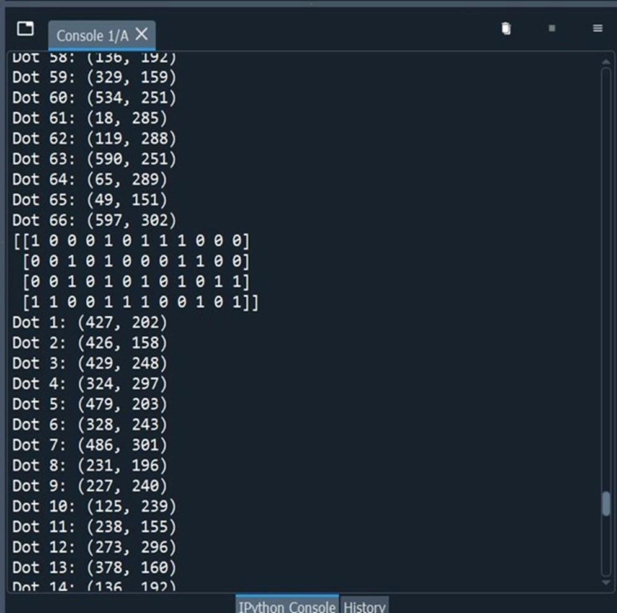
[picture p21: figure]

Dept. of Electrical & Electronics Engineering, PES University | Page 39

The tube head is detected by using input image from the camera after being passed by the trained weights through torch.hub.load().

Figure 29 - Real time detection of tubes

### 8.6. GENERATION OF MATRIX USING PYTHON CODE

By providing pixel coordinates of the first slot, i.e., origin, we can approximately determine the positions of successive slots using slot interval distance also provided. By checking for centroids at these positions, a binary matrix is formed using 1 as a presence flag. Due to the video being dynamic, there are a few errors which are compensated for using carefully computed offset thresholds.

Figure 30 – Matrix Generated

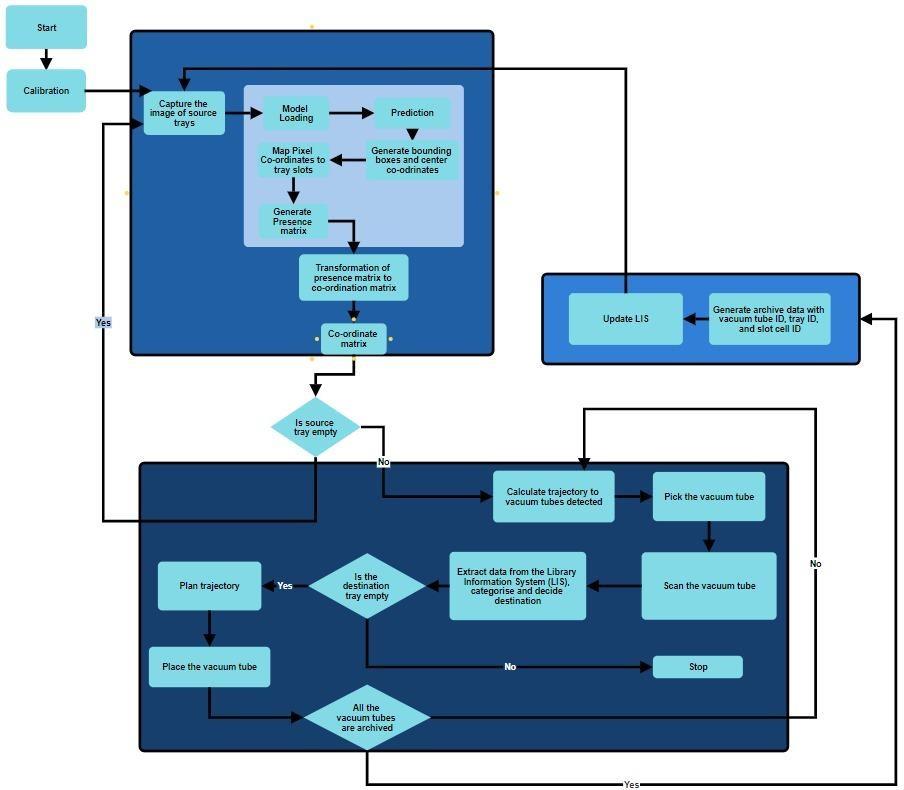
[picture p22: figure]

Dept. of Electrical & Electronics Engineering, PES University | Page 40

### 9. SOFTWARE FLOWCHART

Figure 31 - Software Block diagram

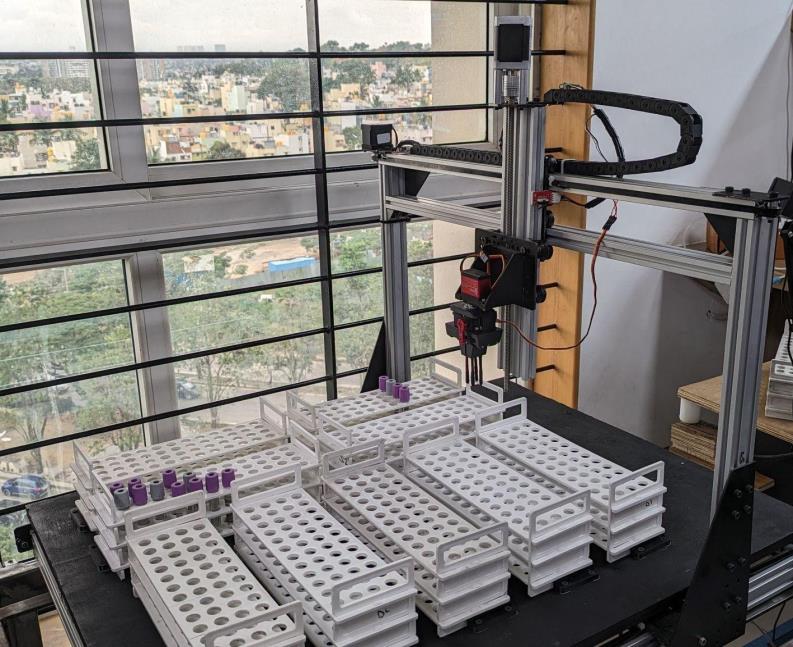
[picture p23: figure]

Dept. of Electrical & Electronics Engineering, PES University | Page 41

### 10. RESULTS

### 10.1. GANTRY

An aluminium structure was used to create a gantry robot. For the movement, we used microcontrollers and actuators. By integrating kinematics and image processing, we developed a fully working gantry robot.

Figure 32 - Side view

Figure 33 - End Gripper

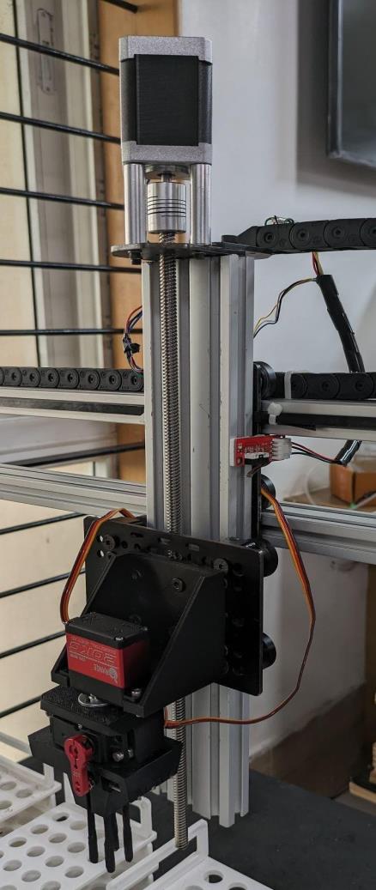
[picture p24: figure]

Dept. of Electrical & Electronics Engineering, PES University | Page 42

Figure 33 - Z axis

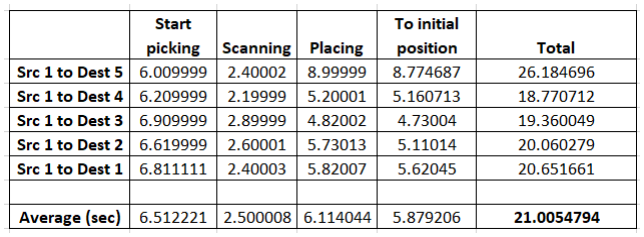
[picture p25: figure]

Dept. of Electrical & Electronics Engineering, PES University | Page 43

### 10.2. RECORDINGS

We have recorded the time required for the entire cycle and the table below shows the average time for each step:

Table 2 - Cycle time recordings

In order to verify the precision of the test tube selection, we have additionally logged experiments:

Table 3 - Trials

### 10.3. CONSTRAINTS OBSERVED

Some of the requirements that we faced while we carried out our project were:

- Object recognition under various lighting conditions and camera angles
- Deferral of the robot
- Spatial accuracy of the end effector
- Detection of the empty slots in the destination rack
- Maintaining a consistent power supply to all the actuators simultaneously
- Preserve the cycle time for pick and place operations consistently

Dept. of Electrical & Electronics Engineering, PES University | Page 44

### 11. CONCLUSION

In conclusion, the pick and place gantry robot used for archiving lab samples in a diagnostic lab is a highly versatile and efficient solution to develop an automated action, reducing the human workload. It offers numerous advantages in terms of accuracy, precision, efficiency, and safety. The use of computer vision significantly helps in identifying the location of the test tubes. Thus, increasing the overall speed and accuracy of the process. Additionally, the system can be feasibly scaled up for handling larger volumes of samples, with the potential to greatly improve the efficiency and throughput of the archiving process.

We have designed a gantry robot using Solid works and assembled the gantry primarily using aluminium extrusions. Also, an end effector was designed and 3D printed for gripping the vacuum tubes for pick and place application. We used YOLO for detecting tubes and NumPy to generate the matrix of the rack. In future, the incorporation of AI and machine learning algorithms will empower gantry robots to adapt to dynamic environments, optimise processes, and learn from experience.

Successful implementation of such a system requires careful consideration of factors such as camera placement, lighting conditions and image processing algorithms. However, the use of machine learning technology integration with the gantry system represents a highly promising solution for automating the archiving of lab samples, with the potential to greatly improve the accuracy of laboratory operations.

### 12. FUTURE SCOPE

- The system can be upgraded to perform various other functions in the laboratory such as segregation.
- Implementing a dynamic control for pick and place application.

Dept. of Electrical & Electronics Engineering, PES University | Page 45

### 13. REFERENCES

[1.] M. Karthi, V. Muthulakshmi, R. Priscilla, P. Praveen and K. Vanisri, "Evolution of YOLO-V5 Algorithm for Object Detection: Automated Detection of Library Books and Performance validation of Dataset," 2021 International Conference on Innovative Computing, Intelligent Communication and Smart Electrical Systems (ICSES), Chennai, India, 2021, pp. 1-6, doi: 10.1109/ICSES52305.2021.9633834.

[2.] Song, Q.; Li, S.; Bai, Q.; Yang, J.; Zhang, X.; Li, Z.; Duan, Z. Object Detection Method for Grasping Robot Based on Improved YOLOv5. Micro Machines 2021, 12, 1273.

[3.] J. Černohorský and D. Lindr, "Laboratory gantry robot design and control," Proceedings of the 13th International Carpathian Control Conference (ICCC), High Tatras, Slovakia, 2012, pp. 86-90, doi: 10.1109/CarpathianCC.2012.6228621.

[4.] M. M. Rahman, S. Chakma, D. M. Raza, S. Akter and A. Sattar, "Real-Time Object Detection using Machine Learning," 2021 12th International Conference on Computing Communication and Networking Technologies (ICCCNT), Kharagpur, India, 2021, pp. 1-5

[5.] P. Andhare and S. Rawat, "Pick and place industrial robot controller with computer vision," 2016 International Conference on Computing Communication Control and automation (ICCUBEA), Pune, India, 2016, pp. 1-4, doi: 10.1109/ICCUBEA.2016.7860048.

[6.] C. M. Raj, W. Rajanbabu, T. M, R. M, Manjuladevi. and H. S, "Material Handling Using Pick and Place Robot," 2022 8th International Conference on Smart Structures and Systems (ICSSS), Chennai, India, 2022, pp. 1-6, doi: 10.1109/ICSSS54381.2022.9782275.

8%

### SIMILARITY INDEX

3%

### INTERNET SOURCES

4%

### PUBLICATIONS

5%

### STUDENT PAPERS

1 2%

2 1%

3 <1%

4 <1%

5 <1%

6 <1%

7 <1%

# Archiving lab

ORIGINALITY REPORT

PRIMARY SOURCES

# Submitted to PES University

### Student Paper

Cernohorsky, Josef, and David Lindr.

# "Laboratory gantry robot design and control"

,

# Proceedings of the 13th International

Carpathian Control Conference (ICCC), 2012.

### Publication

# www.3dreality.org

### Internet Source

# Submitted to Babes-Bolyai University

### Student Paper

# www.pe.org.pl

### Internet Source

# "ICT Applications for Smart Cities"

# , Springer Science and Business Media LLC, 2022

### Publication

# Alexandre Calazans Possari, Guilherme

Henrique Silva, Bernardo Sant'Anna Costa,

# Eduardo Almeida Soares et al. "Automated Sorting: Mapping of selective collection

8 <1%

9 <1%

10 <1%

11 <1%

12 <1%

13 <1%

14 <1%

# disposal objects using artificial intelligence"

,

# AtoZ: novas práticas em informação e conhecimento, 2023

### Publication

# Submitted to Muscat College

### Student Paper

# Nitin Kumar, Anuj jain. "A Deep Learning Based Model to Assist Blind People in Their Navigation"

# , Journal of Information Technology Education: Innovations in Practice, 2022

### Publication

# Submitted to University of the West Indies

### Student Paper

# "Proceedings of International Conference on Artificial Intelligence and Communication Technologies (ICAICT 2023)"

# , Springer Science and Business Media LLC, 2024

### Publication

# Submitted to Middlesex University

### Student Paper

# Submitted to Liverpool John Moores University

### Student Paper

# S Sethu Selvi, S Pavithraa, R Dharini, E Chaitra. "A Deep Learning Approach to Classify Drones and Birds"

# , 2022 IEEE 2nd

15 <1%

16 <1%

17 <1%

18 <1%

19 <1%

20 <1%

21 <1%

22 <1%

# Mysore Sub Section International Conference (MysuruCon), 2022

### Publication

# patents.google.com

### Internet Source

# psaspb.upm.edu.my

### Internet Source

# www.cse.cuhk.edu.hk

### Internet Source

# Sheikameer Batcha S, M. P. Mohandass, G

Arun, J. Chitra, Girish Madhaorao Lonare,

# Jaydeep Patil. "AI based Gesture Controlled Smart Bionic Arm"

# , 2023 9th International Conference on Advanced Computing and Communication Systems (ICACCS), 2023

### Publication

# st.robu.in

### Internet Source

# Submitted to University of Technology Bahrain

### Student Paper

# dr.ntu.edu.sg

### Internet Source

# www.ukessays.com

### Internet Source

23 <1%

24 <1%

25 <1%

26 <1%

27 <1%

28 <1%

29 <1%

# Submitted to Higher Education Commission Pakistan

### Student Paper

# Shripad Bhatlawande, Swati Shilaskar, Saket Kumar, Parag Salunkhe, Sarthak Jaybhay. "Car Dent Detection Using Watershed Segmentation and Deep Learning"

, 2023 4th

# International Conference on Smart Electronics and Communication (ICOSEC), 2023

### Publication

# jozilla.net

### Internet Source

# Piccardo, H.R.. "A new approach to on-line path planning and generation for robots in non-static environments"

# , Robotics and Autonomous Systems, 1991

### Publication

# journal-home.s3.ap-northeast-2.amazonaws.com

### Internet Source

# "Computer Vision – ECCV 2018"

# , Springer Science and Business Media LLC, 2018

### Publication

# "Pattern Recognition and Computer Vision"

,
Springer Science and Business Media LLC, 2020

### Publication

E

x

### clu

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
### clu

d

e

### biblio

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
### clu

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
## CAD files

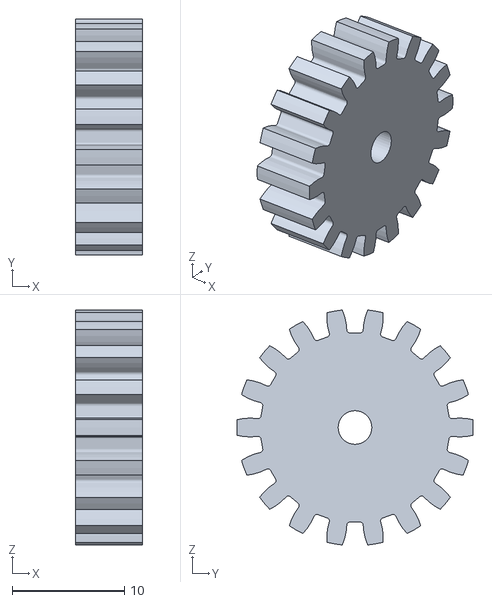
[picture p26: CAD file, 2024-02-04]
hardware/end_effector/main_gear.STL
6.00 x 21.1 x 21.0

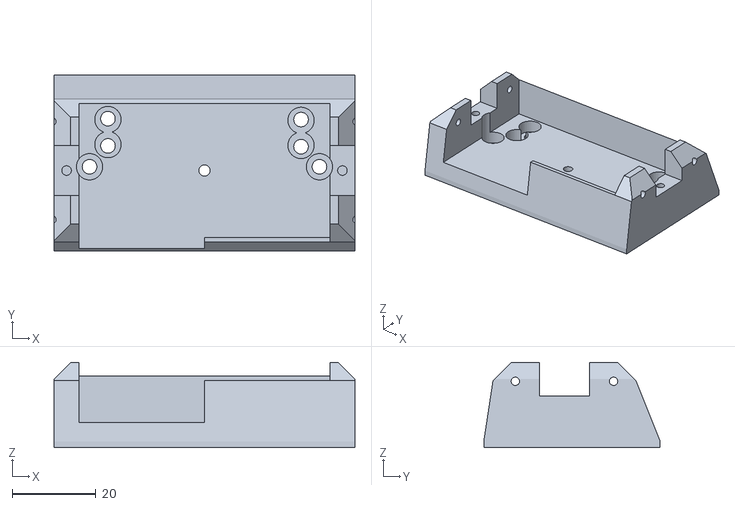
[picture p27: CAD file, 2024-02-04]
hardware/end_effector/base2.STL
72.0 x 42.2 x 20.4

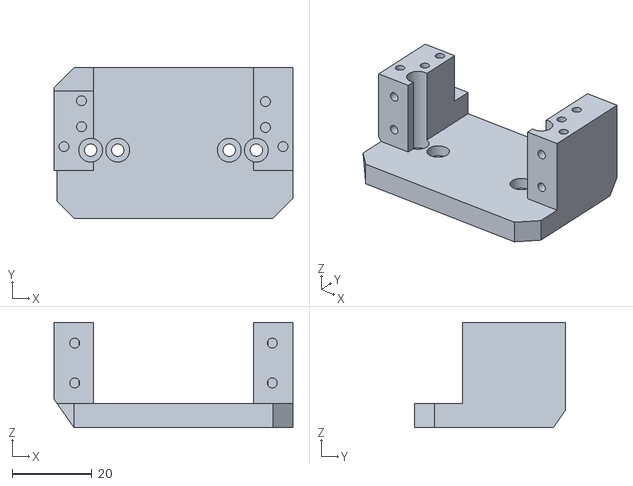
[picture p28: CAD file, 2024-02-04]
hardware/end_effector/base_t.STL
60.0 x 37.8 x 26.4

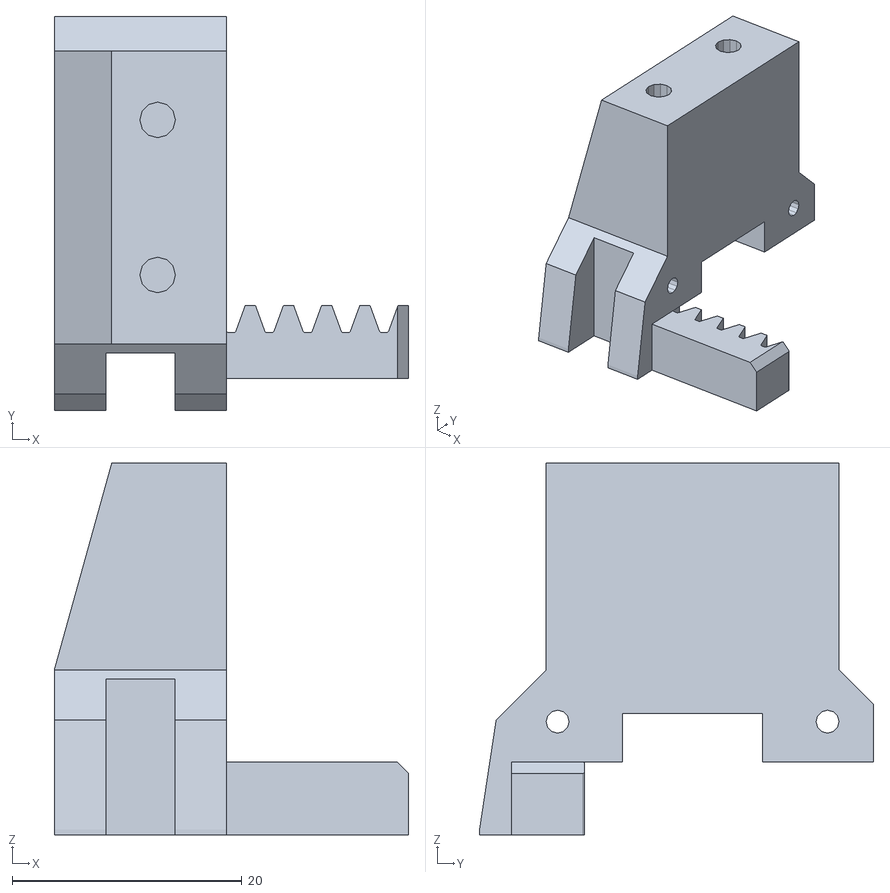
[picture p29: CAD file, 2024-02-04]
hardware/end_effector/jaw1_act_steel_prongs.STL
30.9 x 34.3 x 32.3

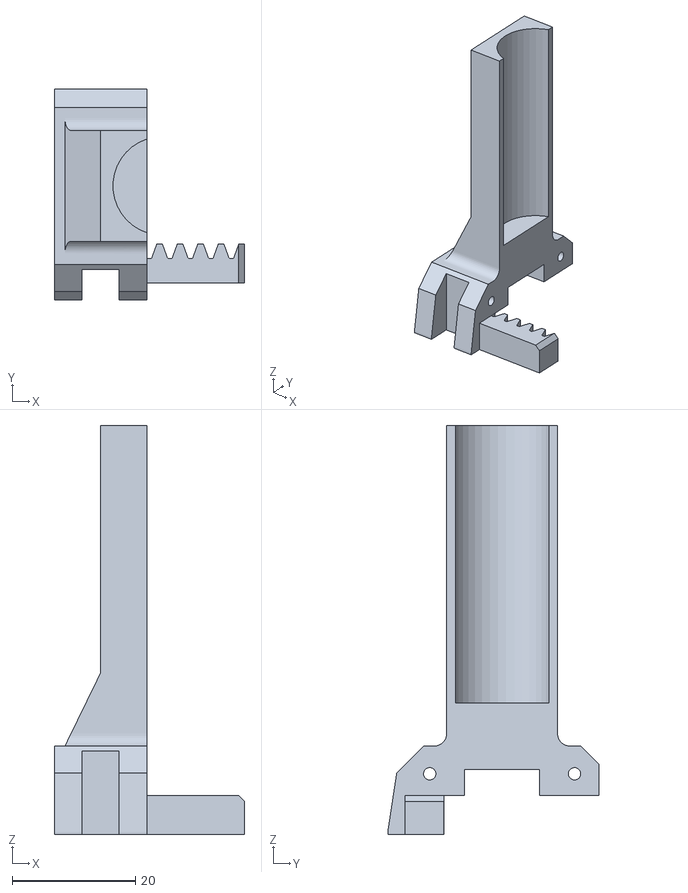
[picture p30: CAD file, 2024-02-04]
hardware/end_effector/jaw1_act.STL
30.9 x 34.3 x 66.3

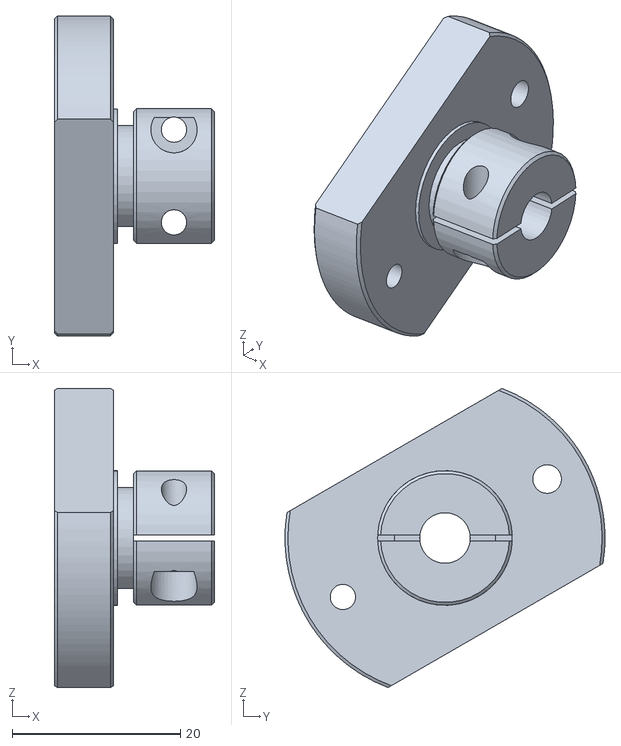
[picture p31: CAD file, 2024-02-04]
hardware/end_effector/coupler.STL
19.0 x 38.0 x 35.5

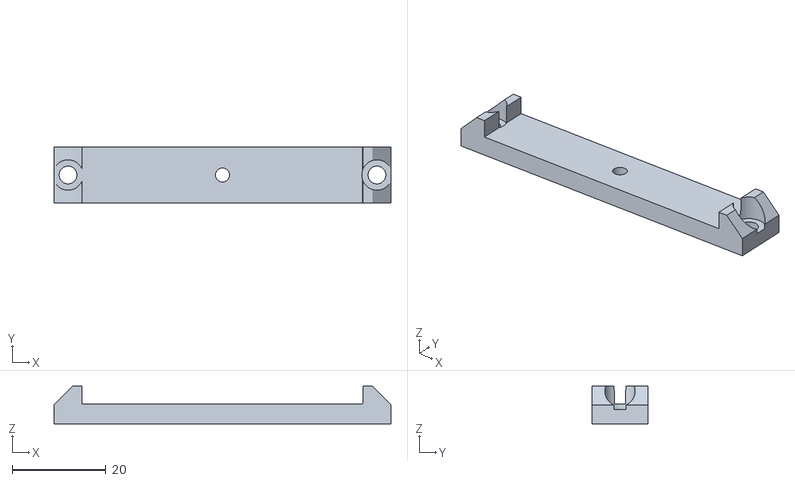
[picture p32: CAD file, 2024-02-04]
hardware/end_effector/center_bridge.STL
72.0 x 12.0 x 8.02

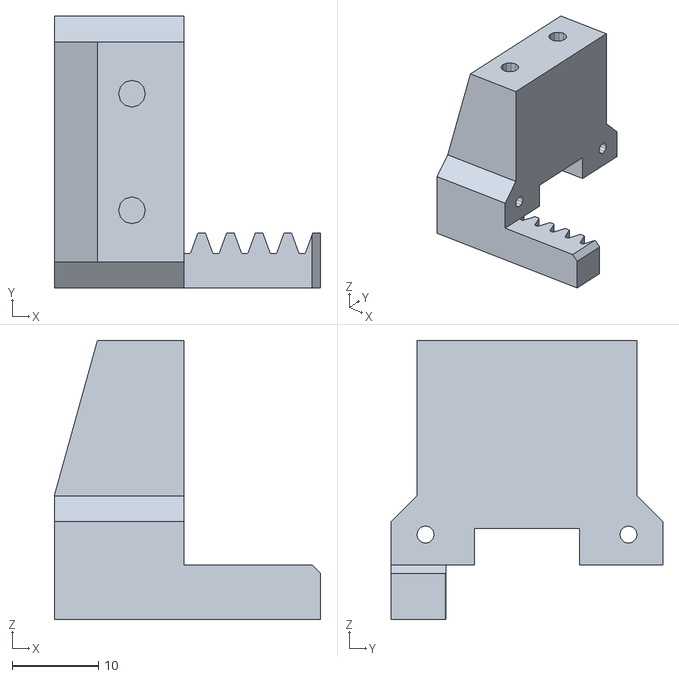
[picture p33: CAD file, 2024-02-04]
hardware/end_effector/jaw2_act_steel_prongs.STL
30.9 x 31.5 x 32.3

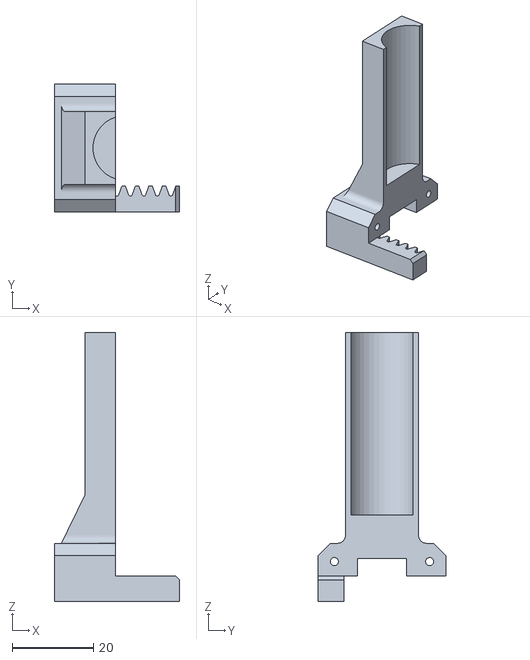
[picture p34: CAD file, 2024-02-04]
hardware/end_effector/jaw2_act.STL
30.9 x 31.5 x 66.4

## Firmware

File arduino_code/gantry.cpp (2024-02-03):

#include <AccelStepper.h>
#include <Servo.h>
#include "gantry.h"


#define xSTEP_PIN 2
#define xDIR_PIN 5
#define xlimit 9

#define ySTEP_PIN 3
#define yDIR_PIN 6
#define ylimit 10

#define zSTEP_PIN 4
#define zDIR_PIN 7
#define zlimit 11


#define INIT_X_HOMING -1
#define INIT_Y_HOMING -1
#define INIT_Z_HOMING -1


const float mmPerRevX = 60;
const float mmPerRevY = 60;
const float mmPerRevZ = 8;

const int stepsPerRevX = 400;
const float stepsPerMmX = stepsPerRevX / mmPerRevX;

const int stepsPerRevY = 800;
const float stepsPerMmY = stepsPerRevY / mmPerRevY;

const int stepsPerRevZ = 400;
const float stepsPerMmZ = stepsPerRevZ / mmPerRevZ;

static Servo servoMotor;  // Create a servo object
const int servoPin = 45;  // Define the servo pin
static int accu_state = 0;

static Servo endServo;  // Create a servo object
const int servoPinR = 44; 

static AccelStepper stepperx(AccelStepper::DRIVER, xSTEP_PIN, xDIR_PIN);
static AccelStepper steppery(AccelStepper::DRIVER, ySTEP_PIN, yDIR_PIN);
static AccelStepper stepperz(AccelStepper::DRIVER, zSTEP_PIN, zDIR_PIN);

// void end_servo_rot(int);

void initSystem()
{

  servoMotor.attach(servoPin);
  servoMotor.write(0);
  
  endServo.attach(servoPinR);
  endServo.write(3);
  
  pinMode(xlimit, INPUT_PULLUP);
  pinMode(ylimit, INPUT_PULLUP);
  pinMode(ylimit, INPUT_PULLUP);

}

void getCurrPos(){
  int xx = stepperx.currentPosition();
  int zz = stepperz.currentPosition();
  int yy = steppery.currentPosition();
}
void goHome(void)
{

  goHomeZ();
  goHomeY();
  goHomeX();


//   stepperx.setMaxSpeed(15000.0);      
//  stepperx.setAcceleration(600.0);

//   steppery.setMaxSpeed(20000.0);      
//  steppery.setAcceleration(1000.0); 

//   stepperz.setMaxSpeed(15000.0);      
//   stepperz.setAcceleration(12000.0);
  stepperx.setMaxSpeed(15000.0);      
 stepperx.setAcceleration(1800.0);

  steppery.setMaxSpeed(20000.0);      
 steppery.setAcceleration(12000.0); 

  stepperz.setMaxSpeed(15000.0);      
  stepperz.setAcceleration(12000.0);
  Serial.println("h");
}
void goHomeX()
{

  delay(5);  

  stepperx.setMaxSpeed(2000.0);      
  stepperx.setAcceleration(2000.0); 

  long initial_homing = INIT_X_HOMING;

  while (digitalRead(xlimit)) {  
      stepperx.moveTo(initial_homing);  
      initial_homing--;
      stepperx.run();  
      delay(2);
  }

  stepperx.setCurrentPosition(0);  
  stepperx.setMaxSpeed(6000.0); 
  stepperx.setAcceleration(3000.0);
  initial_homing= -INIT_X_HOMING;

  while (!digitalRead(xlimit)) { 
    stepperx.moveTo(initial_homing);  
    stepperx.run();
    initial_homing++;
    delay(2);
  }
  
  stepperx.setCurrentPosition(0);

}
void goHomeY()
{

  ///////////////////////////////////////////////////////////
  delay(5);  

  steppery.setMaxSpeed(3000.0);      
  steppery.setAcceleration(2000.0); 

  long initial_homing = INIT_Y_HOMING;

  while (digitalRead(ylimit)) {  
      steppery.moveTo(initial_homing);  
      initial_homing--;
      steppery.run();  
      delay(2);
  }

  steppery.setCurrentPosition(0);  
  steppery.setMaxSpeed(6000.0);
  steppery.setAcceleration(3000.0);
  
  initial_homing = -INIT_Y_HOMING;

  while (!digitalRead(ylimit)) { 
    steppery.moveTo(initial_homing);  
    steppery.run();
    initial_homing++;
    delay(2);
  }
  
  steppery.setCurrentPosition(0);
///////////////////////////////////////////////////////////////

}
void goHomeZ()
{

  delay(5);  

  stepperz.setMaxSpeed(4000.0);      
  stepperz.setAcceleration(1000.0);
  

  long initial_homing = INIT_Z_HOMING;

  while (digitalRead(zlimit)) {  
      stepperz.moveTo(initial_homing);  
      initial_homing--;
      stepperz.run();  
      delay(2);
  }

  stepperz.setCurrentPosition(0);  
  stepperz.setMaxSpeed(6000.0);    
  stepperz.setAcceleration(3000.0);
  
  initial_homing=-INIT_Z_HOMING ;

  while (!digitalRead(zlimit)) { 
    stepperz.moveTo(initial_homing);  
    stepperz.run();
    initial_homing++;
    delay(2);
  }
  
  stepperz.setCurrentPosition(0);


//////////////////////////////////////////////////////////////

}



#define MAX_X_STEPS   7000

void goToX(float x_in)
{
    int stepsToMoveX = int(x_in * stepsPerMmX);
    if (stepsToMoveX >MAX_X_STEPS) 
        stepsToMoveX = MAX_X_STEPS;

    stepperx.moveTo(stepsToMoveX);
    // stepperx.setSpeed(5000);
    while (stepperx.distanceToGo() != 0) {
        stepperx.run();
  
    }

}

#define MAX_Y_STEPS   11000
void goToY(float y_in)
{
    int stepsToMoveY = int(y_in * stepsPerMmY); 
    if (stepsToMoveY >MAX_Y_STEPS) 
        stepsToMoveY = MAX_Y_STEPS;

    steppery.moveTo(stepsToMoveY);
    while (steppery.distanceToGo() != 0) {
        steppery.run();
      
    }
}

#define MAX_Z_STEPS   8500

void goToZ(float z_in)
{
    int stepsToMoveZ = int(z_in * stepsPerMmZ);
    if (stepsToMoveZ >MAX_Z_STEPS) 
        stepsToMoveZ = MAX_Z_STEPS;

    stepperz.moveTo(stepsToMoveZ);
    while (stepperz.distanceToGo() != 0) {
        stepperz.run();
    }

}
void goToXYZ(float x_in, float y_in, float z_in, bool oneByOne_in)
{
   if (oneByOne_in == true)
   {
     goToZ(z_in);
     goToY(y_in);
     goToX(x_in);
//     if (xDone == true && zDone == true && yDone == true){
      Serial.println("d");
//     }
   }
   else
   {
      // goToZ(z_in);
      int stepsToMoveX = int(x_in * stepsPerMmX);
      int stepsToMoveY = int(y_in * stepsPerMmY); 
      int stepsToMoveZ = int(z_in * stepsPerMmZ);
      stepperx.moveTo(stepsToMoveX);
      steppery.moveTo(stepsToMoveY);
      stepperz.moveTo(stepsToMoveZ);

      bool xDone = false;
      bool yDone = false;
      bool zDone = false;
      
      while ((xDone==false) || (yDone==false) || (zDone == false))
      {
        if (zDone == false)
        {
             if (stepperz.distanceToGo() != 0) 
                 stepperz.run();
             else
                 zDone = true;
        }
        if (xDone == false)
        {
             if (stepperx.distanceToGo() != 0) 
                 stepperx.run();
             else
                 xDone = true;
        }
        if (yDone == false)
        {
             if (steppery.distanceToGo() != 0) 
                 steppery.run();
             else
                 yDone = true;
        }

      }
      if (xDone == true && zDone == true && yDone == true){
    Serial.println("d");
}
    }
    
}

void goTozXY(float x_in, float y_in, float z_in){
  int stepsToMoveX = int(x_in * stepsPerMmX);
  int stepsToMoveY = int(y_in * stepsPerMmY); 
  int stepsToMoveZ = int(z_in * stepsPerMmZ);
  stepperx.moveTo(stepsToMoveX);
  steppery.moveTo(stepsToMoveY);
  stepperz.moveTo(stepsToMoveZ);

  bool xDone = false;
  bool yDone = false;
  bool zDone = false;
      
      while ((xDone==false) || (yDone==false))
      {
        if (xDone == false)
        {
             if (stepperx.distanceToGo() != 0) 
                 stepperx.run();
             else
                 xDone = true;
        }
        if (yDone == false)
        {
             if (steppery.distanceToGo() != 0) 
                 steppery.run();
             else
                 yDone = true;
        }
        

}

while(zDone==false){

  if (zDone == false)
        {
             if (stepperz.distanceToGo() != 0) 
                 stepperz.run();
             else
                 zDone = true;
        }
}
if (xDone == true && zDone == true && yDone == true){
  Serial.println("d");
}
}
void goToXYandZ(float x_in, float y_in, float z_in){
  int stepsToMoveX = int(x_in * stepsPerMmX);
  int stepsToMoveY = int(y_in * stepsPerMmY); 
  int stepsToMoveZ = int(z_in * stepsPerMmZ);
  stepperx.moveTo(stepsToMoveX);
  steppery.moveTo(stepsToMoveY);
  stepperz.moveTo(stepsToMoveZ);

  bool xDone = false;
  bool yDone = false;
  bool zDone = false;
  while(zDone==false){

  if (zDone == false)
        {
             if (stepperz.distanceToGo() != 0) 
                 stepperz.run();
             else
                 zDone = true;
        }
}
while ((xDone==false) || (yDone==false))
      {
        if (xDone == false)
        {
             if (stepperx.distanceToGo() != 0) 
                 stepperx.run();
             else
                 xDone = true;
        }
        if (yDone == false)
        {
             if (steppery.distanceToGo() != 0) 
                 steppery.run();
             else
                 yDone = true;
        }
              
  

}


}

//#define GRIP_OPEN_ROTATION  25
void gripperOpen(int grip)
{
  servoMotor.write(grip);

}

//#define GRIP_CLOSE_ROTATION  5

void gripperClose(int grip)
{
  servoMotor.write(grip);
  delay(200);
  Serial.println("e");

}

void end_servo_rot(int grip)
{
  endServo.write(grip);
  delay(500);
  Serial.println("e");
}

void goToSource(int x_in,int y_in,int z_in){

  gripperOpen(18);
  
  goTozXY(x_in,y_in,z_in);
  if(stepperz.distanceToGo() ==0){
//   gripperClose(0);
//   delay(1000);
    }
  
}

void goToDest(int x_in,int y_in,int z_in){
  goToZ(100);
  goTozXY( x_in, y_in,z_in);
  if(stepperz.distanceToGo() ==0){
    gripperOpen(18);
    delay(500);
    goToZ(100);
    }

}


void goStepsX(int stepx_in)
{

}
void goStepsY(int stepy_in)
{


}
void goStepsZ(int stepz_in)
{

}
void goStepsXYZ(int stepx_in, int stepy_in, int stepz_in)
{

}

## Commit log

2023-12-22 Rotation and Barcode
    [reg_tt_dataset.csv]
2024-02-03 Upload CAD and Arduino code
    [d_database_dept.csv, reg_tt_dataset.csv]
2024-02-04 Uploaded end effector STLs
    [base2.STL, base_t.STL, center_bridge.STL, coupler.STL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]
